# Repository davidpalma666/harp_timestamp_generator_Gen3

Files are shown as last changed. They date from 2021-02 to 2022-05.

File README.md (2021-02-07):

# Harp Timestamp Generator Gen3

This device generates programable timestamps to up to 6 harp devices.

Includes an internal battery to increase reliability for long term experiments.

# Licensing

The code, designs, documentation, and photos available in this repository is free: you can redistribute it and/or modify it under the terms of the used license.
Each subdirectory will contain a license or, possibly, a set of licenses if it involves both hardware and software. Check files named LICENSE.

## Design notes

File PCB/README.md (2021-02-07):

# Harp Timestamp Generator Gen1

## Licensing

The designs, documentation, and photos available in this repository are free: you can redistribute it and/or modify it under the terms of the used license.
Check file named LICENSE.

Copyright OEPS 2021

<br />This work is licensed under a <a rel="license" href="http://creativecommons.org/licenses/by-nc-sa/3.0/igo/">Creative Commons Attribution-NonCommercial-ShareAlike 3.0 IGO License</a>.

If your are interested in obtaining a license to sell this device, please contact info@oeps.tech

[1]: https://docs.google.com/spreadsheets/d/1aobmmEzBDethzIlrm1eg0eYkBqlyX3s9WbA9KgRwVQI/edit?usp=sharing

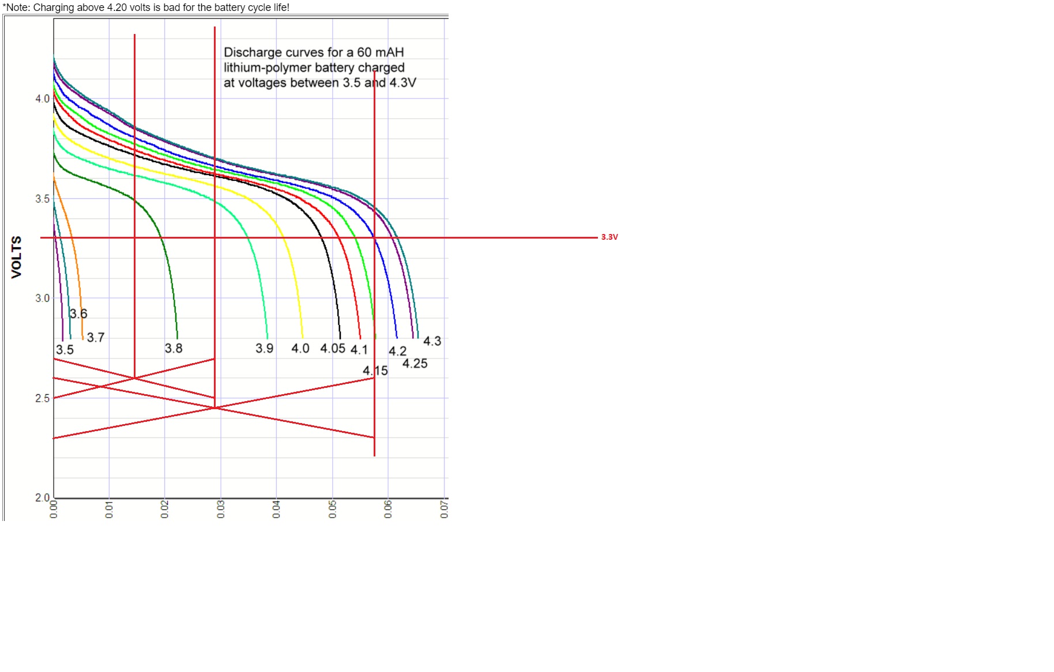
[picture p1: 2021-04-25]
Firmware/battery discharge curve.jpg

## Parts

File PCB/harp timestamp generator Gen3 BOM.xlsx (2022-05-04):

Qty | Value | Package | Parts | MPN | Type | Distributor | Distributor PN
ASSEMBLY HOUSE
1 | CFPA | CFPA | BUTTON | CFPA-1FB4-A2T | SMD | Digikey | 563-1246-1-ND
28 | 100nF | C0402 | C1, C3, C5, C7, C9, C12, C13, C14, C15, C16, C17, C18, C19, C20, C21, C22, C25, C26, C27, C28, C30, C31, C32, C35, C36, C37, C38, C62 | CGA2B3X7R1H104K050BB | SMD | Digikey | 445-6899-1-ND
5 | 4.7uF | C0603 | C8, C10, C11, C23, C24 | CRCW040210R0FKEDHP | SMD | Digikey | 541-10.0YCT-ND
1 | 4.7nF | C0402 | C2 | UMK105B7472KV-F | SMD | Digikey | 587-2237-1-ND
1 | 330nF | C0402 | C29 | GRM155R61A334KE15D | SMD | Digikey | 490-3263-1-ND
2 | 10n | C0402 | C33, C34 | CL05B103KB5NNNC | SMD | Digikey | 1276-1028-1-ND
2 | 47pF | C0402 | C4, C6 | 06035A470JAT2A | SMD | Digikey | 478-1171-1-ND
1 | 100u 25V | TT2D6 | C39 | EEUFM1E101B | TH | Digikey | P19702CT-ND
1 | 330pF | C0402 | C40 | C0402C331J5GACTU | SMD | Digikey | 399-7787-1-ND
7 | CLCK_JACK | 35RASMT2BHNTRX | CLKIN, CLKOUT0, CLKOUT1, CLKOUT2, CLKOUT3, CLKOUT4, CLKOUT5 | 35RASMT2BHNTRX | SMD | Digikey | SC1489-1-ND
1 | 330 Ohms @ 100MHz | R0603 | F1 | BLM18SG331TN1D | SMD | Digikey | 490-3997-1-ND
1 | MCP73831T-2ATI/OT | TSOT23-5 | IC1 | MCP73831T-2ATI/OT | SMD | Digikey | MCP73831T-2ATI/OTCT-ND
3 | SN74LVC1G125DBVT | SOT23-5 | IC10, IC18, IC19 | SN74LVC1G125DBVT | SMD | Digikey | 296-26595-1-ND
6 | SI8621BC-B-IS | SOIC8 | IC12, IC13, IC14, IC15, IC16, IC17 | Si8621BC-B-IS | SMD | Digikey | 336-2064-5-ND | Replacements: SI8621BB-B-IS
1 | USBLC6-2SC6 | SOT23-6L | IC2 | USBLC6-2SC6 | SMD | Digikey | 497-5235-1-ND
1 | FT232RL | SSOP28 | IC3 | FT232RL-REEL | SMD | Digikey | 768-1007-1-ND
1 | ICL7673CBAZA-T | SOIC8 | IC4 | ICL7673CBAZA-T | SMD | Digikey | ICL7673CBAZA-TCT-ND
2 | TLV70033DDCR | TSOT23-5 | IC5, IC11 | TLV70033DDCR | SMD | Digikey | 296-27937-6-ND
1 | ATXMEGA16A4U-AU | QFP80P1200X1200X120-44N | IC6 | ATXMEGA16A4U-AU | SMD | Digikey | ATXMEGA16A4U-AU-ND
3 | M74VHC1GT126DF1G | SC70-5 | IC7, IC8, IC9 | M74VHC1GT126DF1G | SMD | Digikey | M74VHC1GT126DF1GOSCT-ND
1 | 40R@100MHz | R0805 | L1 | MI0805K400R-10 | SMD | Digikey | 240-2389-1-ND
5 | 569-0112-100 | 569-011X-X00_LED_ARRAY | LED1, LED2, LED3, LED4, LED5 | 5690-111-100F | SMD | Digikey | 350-1782-ND
1 | OSCILLATOR | OSCILLATOR_3.2X2.5 | OSC1 | O 32,0-JT32C-A-K-3,3-LF | SMD | Digikey | 1908-1044-1-ND
1 | 2x3_header | MA03-2 | PDI | 67996-206HLF | TH | Digikey | 609-3210-ND
1 | RTU002P02T106 | SOT323 | Q1 | RTU002P02T106 | SMD | Digikey | RTU002P02T106CT-ND
1 | BC817-40W | SOT323-BEC | Q2 | BC817-40W,135 | SMD | Digikey | 1727-6185-1-ND
1 | BC817-40LT1SMD | SOT23-BEC | Q3 | SBC817-40LT1G | SMD | Digikey | SBC817-40LT1GOSCT-ND
1 | DMG1012UW | SOT323 | Q4 | DMG1012UW-7 | SMD | Digikey | DMG1012UW-7DICT-ND
1 | DMP2035U-7 | SOT323 | Q5 | DMP2035U-7 | SMD | Digikey | DMP2035U-7DICT-ND
1 | 1M | R0402 | R1 | CRCW04021M00FKEDC | SMD | Digikey | DMP2035U-7
3 | 100R | R0603 | R10, R11, R12 | RT0603DRD07100RL | SMD | Digikey | 311-100DCT-ND
3 | 4k5 | R0402 | R13, R17, R19 | RT0402BRD074K53L | SMD | Digikey | YAG1444CT-ND
1 | 20R | R2512 | R15 | CRM2512-FX-20R0ELF | SMD | Digikey | 118-CRM2512-FX-20R0ELFCT-ND
1 | 10R | R0402 | R2 | CRCW040210R0FKEDHP | SMD | Digikey | 541-10.0YCT-ND
13 | 1k | R0402 | R14, R21, R22, R23, R24, R25, R27, R28, R29, R30, R31, R54, R55 | CRCW04021K00FKED | SMD | Digikey | 541-1.00KYCT-ND
6 | 10k | R0402 | R3, R7, R9, R16, R18, R50 | CRCW040210K0FKEDC | SMD | Digikey | 541-3959-1-ND
10 | 330R | R0402 | R33, R34, R35, R36, R37, R40, R41, R42, R44, R45 | RC0402FR-07330RL | SMD | Digikey | 311-330LRCT-ND
1 | 51k 0.1% | R0402 | R4 | ERA-2AEB513X | SMD | Digikey | P51KDCCT-ND
1 | 15K 0.1% => 14k7 | R0402 | R5 | RT0402BRD0714K7L | SMD | Digikey | YAG4174CT-ND
2 | 100k | R0402 | R6, R48 | RC0603FR-07100KL | SMD | Digikey | 311-100KHRCT-ND
1 | I/O Header | ML10L | SV1 | SBH11-PBPC-D05-RA-BK | TH | Digikey | S9177-ND
10 | BC850 | SOT23 | T1, T2, T3, T4, T5, T6, T7, T8, T9, T10 | BC850C,215 | SMD | Digikey | 1727-4862-1-ND
1 | mini USB | 240-0002-1 | USB | UX60-MB-5S8 | SMD | Digikey | H2960TR-ND
1 | Switch SPDT | 7101MD9ABE | BATEN | 7101MD9ABE | TH | Digikey | CKN1045-ND
1 | B2B-PH-K-S(LF)(SN) | JST-XH-02-PACKAGE-ROUND-PAD | X1 | B2B-XH-A(LF)(SN) | SMD | Digikey | 455-2247-ND
POST-PRODUCTION
1 |  |  | Front Panel PCB | PCBWAY
1 |  |  | Rear Panel PCB | PCBWAY
1 |  |  | Enclosure | B5-080BK
1 |  |  | Battery lithium Polymer 2 Ah | MIKROE-1120 | - | Farnell | 2786900
4 |  |  | Bumper Cylindrical Dome 9.53mm | SJ-5306-CLEAR-3000/CASE
ACCESSORIES
3 |  |  | 3.5mm stereo jack cable 0.3 m, Black | P312-001 | - | Digikey | TL1621-ND
4 |  |  | 3.5mm stereo jack cable 1.2 m, Black | AV13646 |  | Farnell | 3712278
1 |  |  | 0.9 left angle USB cable | USB2HABM3RA |  | Farnell | 3402895
NOTES
 |  |  |  | Number of unique parts | 46
 |  |  |  | Number of SMD parts | 42
 |  |  |  | Number of TH parts | 4

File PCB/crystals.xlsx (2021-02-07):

Digikey PN | MNF PN | @25C [ppm] | Range of temperatures [ppm] | Supply Change [ppm] | Load Change [ppm] | Aging/year [ppm] |  | Dimensions [mm] | Pinout | Current [mA] | Type
XC2259CT-ND | ECS-TXO-2520-33-320-AN-TR | 2 | 2.5 | 0.2 | 0.2 | 1 | 5.9 | 2.5 x 2.0 | En/Dis, GND, OUT, VDD | 6 | HCMOS TXCO
1908-1044-1-ND | O 32,0-JT32C-A-K-3,3-LF | 0.5 | 2.5 | 0.2 | 0.2 | 1 | 4.4 | 3.2 x 2.5 | En/Dis, GND, OUT, VDD | 4.8 | HCMOS TXCO
50-ECS-TXO-2520MV-320-AN-CT-ND | ECS-TXO-2520MV-320-AN-TR | 1.5 | 2.5 | 0.3 | 0.3 | 1 | 5.6 | 2.5 x 2.0 | En/Dis, GND, OUT, VDD | 6 | CMOS TXCO
50-ECS-TXO-2520MV-320-AY-CT-ND | ECS-TXO-2520MV-320-AY-TR | 1.5 | 2.5 | 0.3 | 0.3 | 1 | 5.6 | 2.5 x 2.0 | En/Dis, GND, OUT, VDD | 6 | CMOS TXCO
50-ECS-TXO-25CSMV-320-BM-CT-ND | ECS-TXO-25CSMV-320-BM-TR | 2 | 1 | 0.2 | 0.2 | 1 | 4.4 | 2.5 x 2.0 | GND, GND, OUT, VDD | 2.5 | Clipped Sinewave TSCO

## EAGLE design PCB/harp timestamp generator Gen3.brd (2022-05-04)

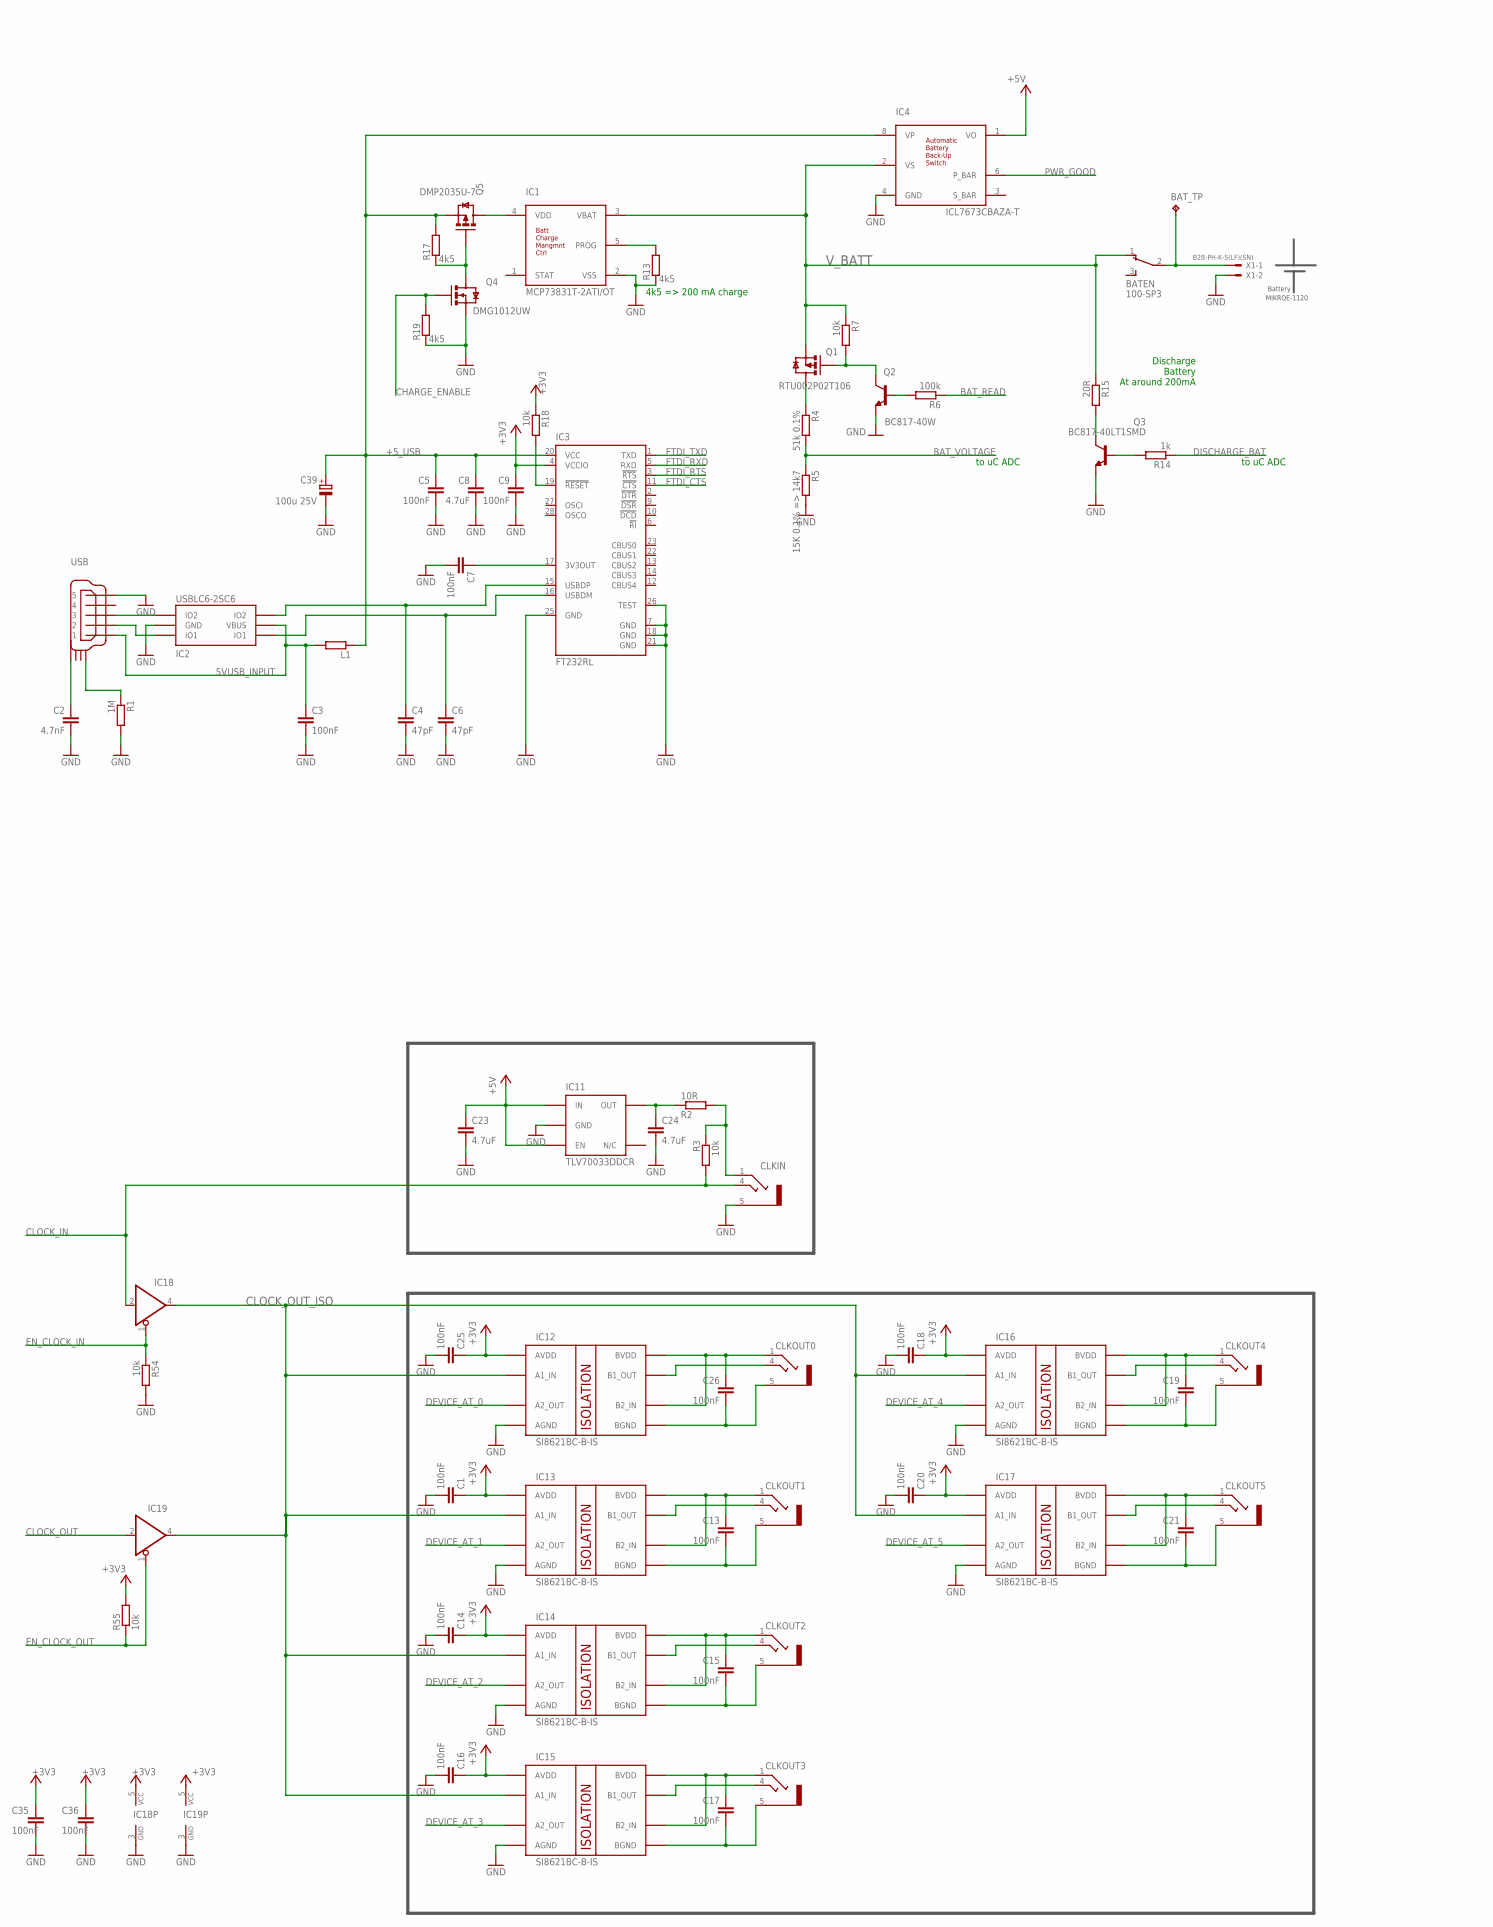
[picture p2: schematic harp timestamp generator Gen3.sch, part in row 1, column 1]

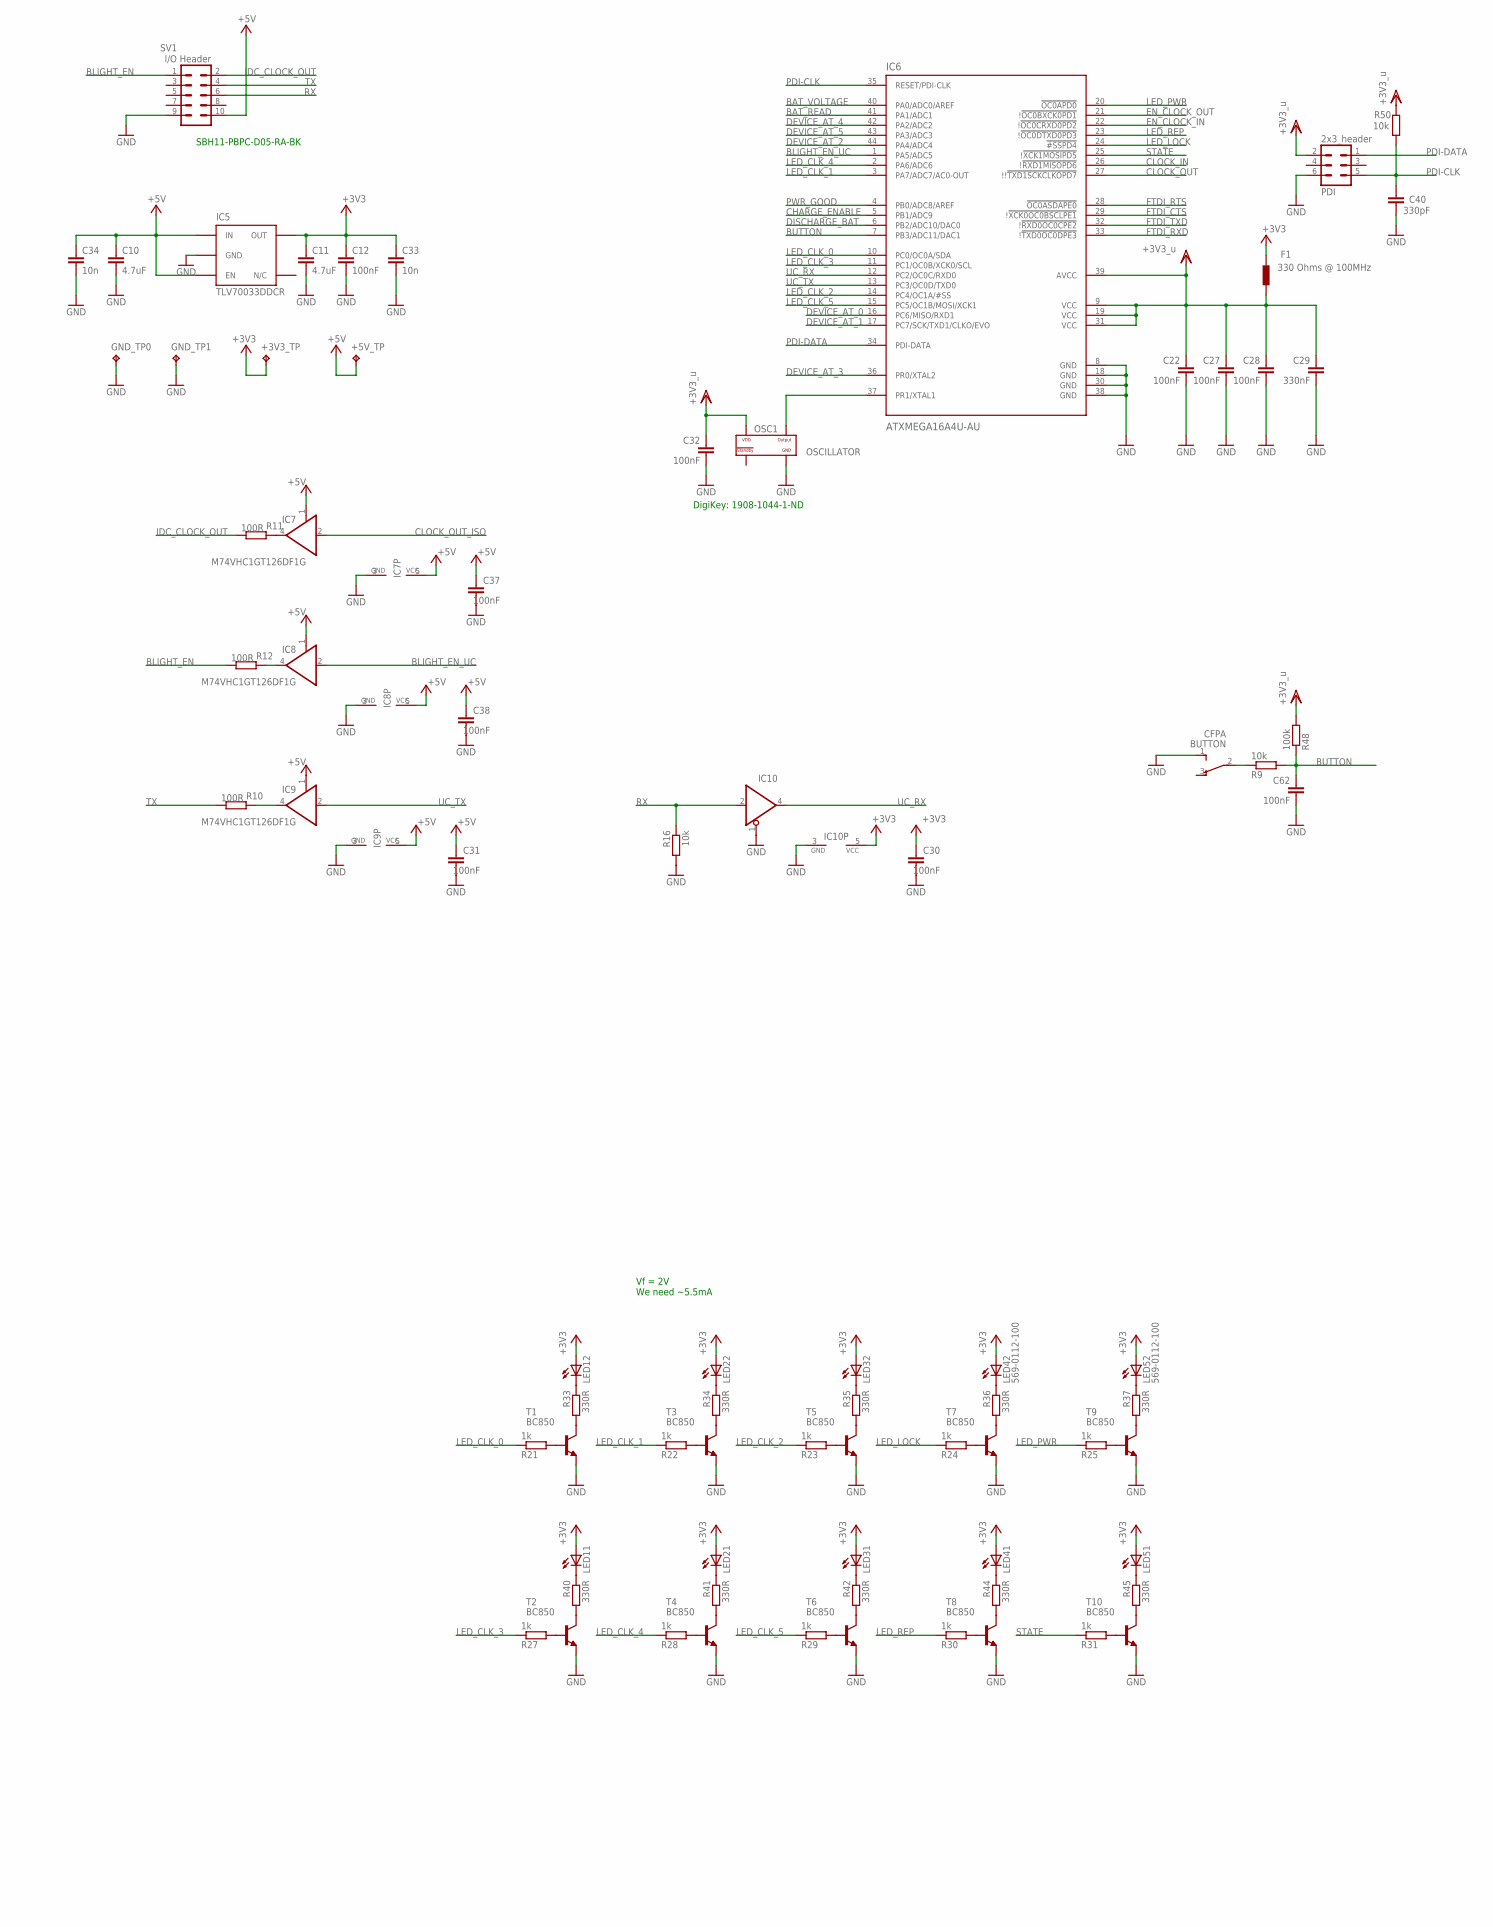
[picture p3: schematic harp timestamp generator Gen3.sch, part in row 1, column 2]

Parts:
+3V3_TP, +5V_TP: TPPAD1-13; P1-13; MPN n.a.
BATEN: 100-SP3; 2M1-SP1-T2-B4-M6RE
BAT_TP: TPPAD1-13; P1-13; MPN n.a.
BUTTON: CFPA; MPN CFPA-1FB4-A2T
C1, C3, C5, C7, C9, C12, C13, C14, C15, C16, C17, C18, C19, C20, C21, C22, C25, C26, C27, C28, C30, C31, C32, C35, C36, C37, C38, C62: 100nF; C0402; MPN CGA2B3X7R1H104K050BB
C2: 4.7nF; C0402; MPN UMK105B7472KV-F
C4, C6: 47pF; C0402; MPN 04025A470JAT2A
C8, C10, C11, C23, C24: 4.7uF; C0603; MPN EMK107ABJ475KA-T
C29: 330nF; C0402; MPN GRM155R61A334KE15D
C33, C34: 10n; C0402; MPN CL05B103KB5NNNC
C39: 100u 25V; TT2D6; MPN EEUFM1E101B
C40: 330pF; C0402; MPN C0402C331J5GACTU
CLKIN: CLCK_JACK; 35RASMT2BHNTRX; MPN 35RASMT2BHNTRX
CLKOUT0, CLKOUT1, CLKOUT2, CLKOUT3, CLKOUT4, CLKOUT5: CLCK_JACK; 35RASMT2BHNTRX; MPN 35RASMT2BHNTRX
F1: 330 Ohms @ 100MHz; R0603; MPN BLM18SG331TN1D
GND_TP0, GND_TP1: TPPAD1-13; P1-13; MPN n.a.
IC1: MCP73831T-2ATI/OT; TSOT23-5
IC2: USBLC6-2SC6; SOT23-6L; MPN USBLC6-2SC6
IC3: FT232RL; SSOP28; MPN FT232RL-REEL
IC4: ICL7673CBAZA-T; SOIC8; MPN ICL7673CBAZA-T
IC5, IC11: TLV70033DDCR; TSOT23-5; MPN TLV70033DDCR
IC6: ATXMEGA16A4U-AU; QFP80P1200X1200X120-44N; MPN ATXMEGA16A4U-AU
IC7, IC8, IC9: M74VHC1GT126DF1G; SC70-5; MPN M74VHC1GT126DF1G
IC10, IC18, IC19: SN74LVC1G125DBVT; SOT23-5; MPN SN74LVC1G125DBVT
IC12, IC13, IC14, IC15, IC16, IC17: SI8621BC-B-IS; SOIC8; MPN Si8621BC-B-IS
L1: 40R@100MHz; R0805; MPN MI0805K400R-10
LED1, LED2, LED3, LED4, LED5: 569-0112-100; 569-011X-X00_LED_ARRAY; MPN 5690-111-100F
OSC1: OSCILLATOR; OSCILLATOR_3.2X2.5; MPN O 32,0-JT32C-A-K-3,3-LF
PDI: 2x3_header; MA03-2; MPN 67996-206HLF
Q1: RTU002P02T106; SOT323; MPN RTU002P02T106
Q2: BC817-40W; SOT323-BEC; MPN BC817-40W,135
Q3: BC817-40LT1SMD; SOT23-BEC; MPN SBC817-40LT1G
Q4: DMG1012UW; SOT323; MPN DMG1012UW-7
Q5: DMP2035U-7; SOT323
R1: 1M; R0402; MPN CRCW04021M00FKEDC
R2: 10R; R0402; MPN CRCW040210R0FKEDHP
R3, R7, R9, R16, R18: 10k; R0402; MPN CRCW040210K0FKEDC
R4: 51k 0.1%; R0402; MPN ERA-2AEB513X
R5: 15K 0.1% => 14k7; R0402; MPN RT0402BRD0714K7L
R6, R48: 100k; R0402; MPN ERJ-2RHD1002X
R10, R11, R12: 100R; R0603; MPN RT0603DRD07100RL
R13, R17, R19: 4k5; R0402; MPN RT0402BRD074K53L
R14: 1k; R0402; MPN CRCW040210K0FKEDC
R15: 20R; R2512; MPN RCP2512W25R0GEB
R21, R22, R23, R24, R25, R27, R28, R29, R30, R31: 1k; R0402; MPN CRCW04021K00FKEDHP
R33, R34, R35, R36, R37, R40, R41, R42, R44, R45: 330R; R0402; MPN RC0402FR-07330RL
R50: 10k; R0402; MPN CRCW040210K0FKED
R54, R55: 10k; R0402; MPN CRCW04021K00FKEDHP
SV1: I/O Header; ML10L; MPN SBH11-PBPC-D05-RA-BK
T1, T2, T3, T4, T5, T6, T7, T8, T9, T10: BC850; SOT23; MPN BC850C,215
USB: mini USB; 240-0002-1; MPN UX60-MB-5S8
X1: B2B-PH-K-S(LF)(SN); JST-XH-02-PACKAGE-ROUND-PAD; MPN B2B-PH-K-S(LF)(SN)

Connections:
5VUSB_INPUT: C3.1, IC2.P$5 (VBUS), L1.2, USB.P$1 (1)
+3V3: +3V3_TP.TP, C1.1, C9.1, C11.1, C12.1, C14.1, C16.1, C18.1, C20.1, C25.1, C30.1, C33.1, C35.1, C36.1, F1.2, IC3.4 (VCCIO), IC5.5 (OUT), IC10.5 (VCC), IC12.1 (AVDD), IC13.1 (AVDD), IC14.1 (AVDD), IC15.1 (AVDD), IC16.1 (AVDD), IC17.1 (AVDD), IC18.5 (VCC), IC19.5 (VCC), LED1.A1 (A), LED1.A2 (A), LED2.A1 (A), LED2.A2 (A), LED3.A1 (A), LED3.A2 (A), LED4.A1 (A), LED4.A2 (A), LED5.A1 (A), LED5.A2 (A), R18.1, R55.2
+5V: +5V_TP.TP, C10.1, C23.1, C31.1, C34.1, C37.1, C38.1, IC4.1 (VO), IC5.1 (IN), IC5.3 (EN), IC7.1 (OE), IC7.5 (VCC), IC8.1 (OE), IC8.5 (VCC), IC9.1 (OE), IC9.5 (VCC), IC11.1 (IN), IC11.3 (EN), SV1.10
+5_USB: C5.1, C8.1, C39.+, IC3.20 (VCC), IC4.8 (VP), L1.1, Q5.1 (S), R17.2
BAT_READ: IC6.41 (PA1/ADC1), R6.1
BAT_VOLTAGE: IC6.40 (PA0/ADC0/AREF), R4.2, R5.1
BLIGHT_EN: R12.1, SV1.1
BLIGHT_EN_UC: IC6.1 (PA5/ADC5), IC8.2 (I)
BUTTON: C62.1, IC6.7 (PB3/ADC11/DAC1), R9.2, R48.1
CHARGE_ENABLE: IC6.5 (PB1/ADC9), Q4.2 (G), R19.2
CLKOUT0: CLKOUT0.4, IC12.7 (B1_OUT)
CLKOUT1: CLKOUT1.4, IC13.7 (B1_OUT)
CLKOUT2: CLKOUT2.4, IC14.7 (B1_OUT)
CLKOUT3: CLKOUT3.4, IC15.7 (B1_OUT)
CLKOUT4: CLKOUT4.4, IC16.7 (B1_OUT)
CLKOUT5: CLKOUT5.4, IC17.7 (B1_OUT)
CLOCK_IN: CLKIN.4, IC6.26 (!!RXD1MISOPD6), IC18.2 (I), R3.2
CLOCK_OUT: IC6.27 (!!!TXD1SCKCLKOPD7), IC19.2 (I)
CLOCK_OUT_ISO: IC7.2 (I), IC12.2 (A1_IN), IC13.2 (A1_IN), IC14.2 (A1_IN), IC15.2 (A1_IN), IC16.2 (A1_IN), IC17.2 (A1_IN), IC18.4 (O), IC19.4 (O)
DEVICE_AT_0: IC6.16 (PC6/MISO/RXD1), IC12.3 (A2_OUT)
DEVICE_AT_1: IC6.17 (PC7/SCK/TXD1/CLKO/EVO), IC13.3 (A2_OUT)
DEVICE_AT_2: IC6.44 (PA4/ADC4), IC14.3 (A2_OUT)
DEVICE_AT_3: IC6.36 (PR0/XTAL2), IC15.3 (A2_OUT)
DEVICE_AT_4: IC6.42 (PA2/ADC2), IC16.3 (A2_OUT)
DEVICE_AT_5: IC6.43 (PA3/ADC3), IC17.3 (A2_OUT)
DISCHARGE_BAT: IC6.6 (PB2/ADC10/DAC0), R14.1
EN_CLOCK_IN: IC6.22 (!!OC0CRXD0PD2), IC18.1 (OE), R54.1
EN_CLOCK_OUT: IC6.21 (!!OC0BXCK0PD1), IC19.1 (OE), R55.1
FTDI_CTS: IC3.11 (!CTS), IC6.29 (!!XCK0OC0BSCLPE1)
FTDI_RTS: IC3.3 (!RTS), IC6.28 (!OC0ASDAPE0)
FTDI_RXD: IC3.5 (RXD), IC6.33 (!!TXD0OC0DPE3)
FTDI_TXD: IC3.1 (TXD), IC6.32 (!!RXD0OC0CPE2)
GND: BUTTON.1 (3), C1.2, C2.2, C3.2, C4.2, C5.2, C6.2, C7.2, C8.2, C9.2, C10.2, C11.2, C12.2, C14.2, C16.2, C18.2, C20.2, C22.2, C23.2, C24.2, C25.2, C27.2, C28.2, C29.2, C30.2, C31.2, C32.2, C33.2, C34.2, C35.2, C36.2, C37.2, C38.2, C39.-, C40.2, C62.2, CLKIN.5, GND_TP0.TP, GND_TP1.TP, IC1.2 (VSS), IC2.P$2 (GND), IC3.7 (GND), IC3.18 (GND), IC3.21 (GND), IC3.25 (GND), IC3.26 (TEST), IC4.4 (GND), IC5.2 (GND), IC6.8 (GND), IC6.18 (GND), IC6.30 (GND), IC6.38 (GND), IC7.3 (GND), IC8.3 (GND), IC9.3 (GND), IC10.1 (OE), IC10.3 (GND), IC11.2 (GND), IC12.4 (AGND), IC13.4 (AGND), IC14.4 (AGND), IC15.4 (AGND), IC16.4 (AGND), IC17.4 (AGND), IC18.3 (GND), IC19.3 (GND), OSC1.P$2 (GND), PDI.6, Q2.E, Q3.E, Q4.1 (S), R1.2, R5.2, R13.1, R16.2, R19.1, R54.2, SV1.9, T1.2 (E), T2.2 (E), T3.2 (E), T4.2 (E), T5.2 (E), T6.2 (E), T7.2 (E), T8.2 (E), T9.2 (E), T10.2 (E), USB.P$5 (5), X1.2
GND_ISO: C26.2, CLKOUT0.5, IC12.5 (BGND)
GND_ISO1: C13.2, CLKOUT1.5, IC13.5 (BGND)
GND_ISO2: C15.2, CLKOUT2.5, IC14.5 (BGND)
GND_ISO3: C17.2, CLKOUT3.5, IC15.5 (BGND)
GND_ISO4: C19.2, CLKOUT4.5, IC16.5 (BGND)
GND_ISO5: C21.2, CLKOUT5.5, IC17.5 (BGND)
IDC_CLOCK_OUT: R11.1, SV1.2
LED_CLK_0: IC6.10 (PC0/OC0A/SDA), R21.1
LED_CLK_1: IC6.3 (PA7/ADC7/AC0-OUT), R22.1
LED_CLK_2: IC6.14 (PC4/OC1A/#SS), R23.1
LED_CLK_3: IC6.11 (PC1/OC0B/XCK0/SCL), R27.1
LED_CLK_4: IC6.2 (PA6/ADC6), R28.1
LED_CLK_5: IC6.15 (PC5/OC1B/MOSI/XCK1), R29.1
LED_LOCK: IC6.24 (!#SSPD4), R24.1
LED_PWR: IC6.20 (!OC0APD0), R25.1
LED_REP: IC6.23 (!!OC0DTXD0PD3), R30.1
unnamed: R24.2, T7.1 (B)
unnamed: Q4.3 (D), Q5.2 (G), R17.1
unnamed: IC8.4 (O), R12.2
unnamed: IC9.4 (O), R10.2
unnamed: C26.1, CLKOUT0.1, IC12.6 (B2_IN), IC12.8 (BVDD)
unnamed: C13.1, CLKOUT1.1, IC13.6 (B2_IN), IC13.8 (BVDD)
unnamed: R36.2, T7.3 (C)
unnamed: IC7.4 (O), R11.2
unnamed: IC1.4 (VDD), Q5.3 (D)
unnamed: C15.1, CLKOUT2.1, IC14.6 (B2_IN), IC14.8 (BVDD)
unnamed: R22.2, T3.1 (B)
unnamed: IC1.5 (PROG), R13.2
unnamed: R21.2, T1.1 (B)
unnamed: LED3.C1 (C), R42.1
unnamed: R33.2, T1.3 (C)
unnamed: R27.2, T2.1 (B)
unnamed: R34.2, T3.3 (C)
unnamed: R40.2, T2.3 (C)
unnamed: LED3.C2 (C), R35.1
unnamed: R28.2, T4.1 (B)
unnamed: R41.2, T4.3 (C)
unnamed: R23.2, T5.1 (B)
unnamed: R35.2, T5.3 (C)
unnamed: R29.2, T6.1 (B)
unnamed: R42.2, T6.3 (C)
unnamed: LED1.C2 (C), R33.1
unnamed: LED2.C2 (C), R34.1
unnamed: LED1.C1 (C), R40.1
unnamed: LED2.C1 (C), R41.1
unnamed: R30.2, T8.1 (B)
unnamed: Q3.B, R14.2
unnamed: Q3.C, R15.2
unnamed: C17.1, CLKOUT3.1, IC15.6 (B2_IN), IC15.8 (BVDD)
unnamed: C7.1, IC3.17 (3V3OUT)
unnamed: IC2.P$1 (IO1), USB.P$2 (2)
unnamed: CLKIN.1, R2.2, R3.1
unnamed: C24.1, IC11.5 (OUT), R2.1
unnamed: BUTTON.2, R9.1
unnamed: C19.1, CLKOUT4.1, IC16.6 (B2_IN), IC16.8 (BVDD)
unnamed: R44.2, T8.3 (C)
unnamed: C21.1, CLKOUT5.1, IC17.6 (B2_IN), IC17.8 (BVDD)
unnamed: IC2.P$3 (IO2), USB.P$3 (3)
unnamed: R25.2, T9.1 (B)
unnamed: R37.2, T9.3 (C)
unnamed: R31.2, T10.1 (B)
unnamed: C2.1, USB.SHIELD_4
unnamed: R45.2, T10.3 (C)
unnamed: R1.1, USB.SHIELD_1
unnamed: LED5.C1 (C), R45.1
unnamed: LED5.C2 (C), R37.1
unnamed: LED4.C2 (C), R36.1
unnamed: LED4.C1 (C), R44.1
unnamed: BATEN.2, BAT_TP.TP, X1.1
unnamed: Q1.3 (D), R4.1
unnamed: Q1.2 (G), Q2.C, R7.2
unnamed: Q2.B, R6.2
unnamed: IC3.19 (!RESET), R18.2
OSC1: IC6.37 (PR1/XTAL1), OSC1.P$3 (OUTPUT)
PDI-CLK: C40.1, IC6.35 (RESET/PDI-CLK), PDI.5, R50.1
PDI-DATA: IC6.34 (PDI-DATA), PDI.1
PWR_GOOD: IC4.6 (P_BAR), IC6.4 (PB0/ADC8/AREF)
RX: IC10.2 (I), R16.1, SV1.6
STATE: IC6.25 (!!XCK1MOSIPD5), R31.1
TX: R10.1, SV1.4
UC_RX: IC6.12 (PC2/OC0C/RXD0), IC10.4 (O)
UC_TX: IC6.13 (PC3/OC0D/TXD0), IC9.2 (I)
USBDM: C6.1, IC2.P$6 (IO1), IC3.16 (USBDM)
USBDP: C4.1, IC2.P$4 (IO2), IC3.15 (USBDP)
VDD: C22.1, C27.1, C28.1, C29.1, C32.1, F1.1, IC6.9 (VCC), IC6.19 (VCC), IC6.31 (VCC), IC6.39 (AVCC), OSC1.P$4 (VDD), PDI.2, R48.2, R50.2
V_BATT: BATEN.1, IC1.3 (VBAT), IC4.2 (VS), Q1.1 (S), R7.1, R15.1

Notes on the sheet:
Vf = 2V We need ~5.5mA
SBH11-PBPC-D05-RA-BK
4k5 => 200 mA charge
Battery
to uC ADC
MIKROE-1120
Discharge Battery At around 200mA
DigiKey: 1908-1044-1-ND

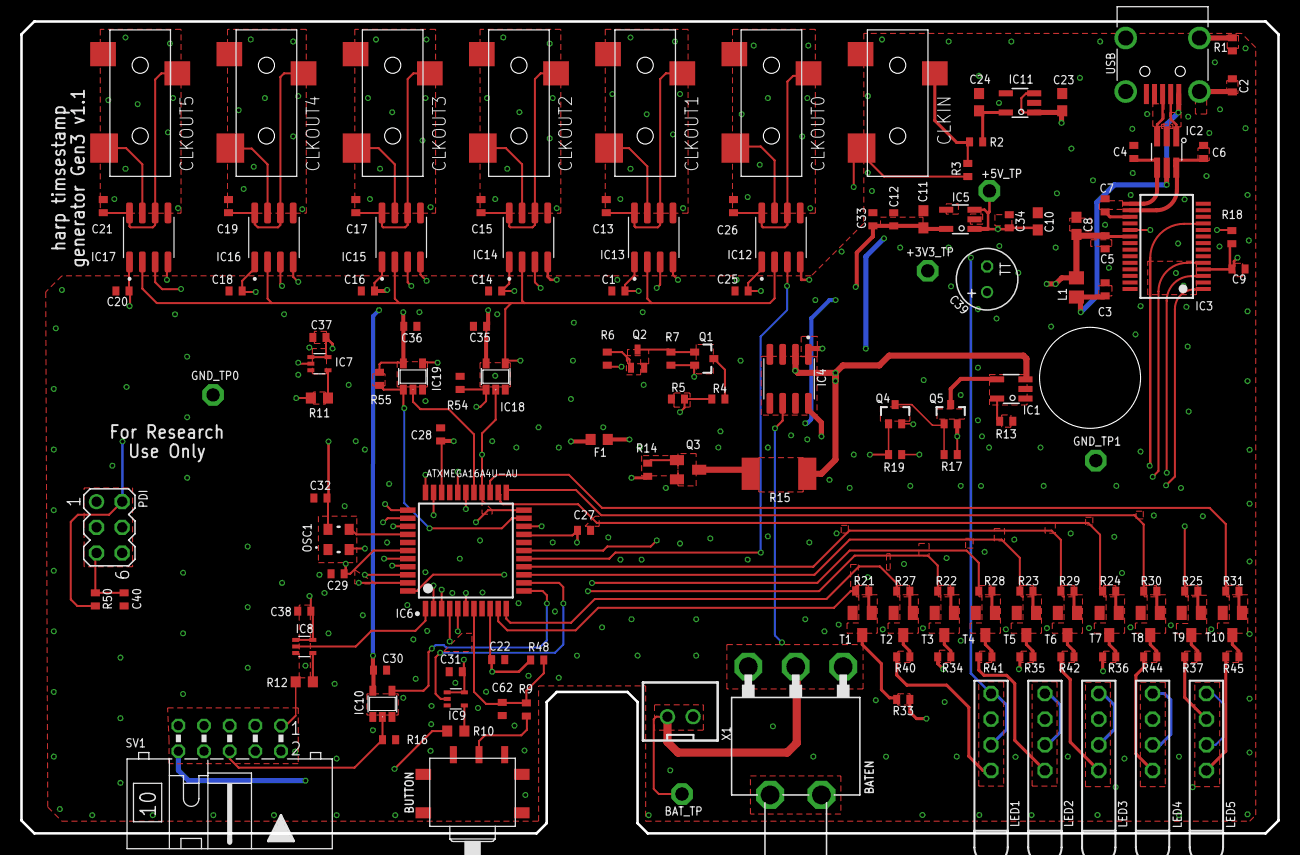
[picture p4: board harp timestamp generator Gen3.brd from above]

Board: 4 copper layers, 124.5 x 80.4 mm, 143 parts (0 on the bottom side), 119 nets.

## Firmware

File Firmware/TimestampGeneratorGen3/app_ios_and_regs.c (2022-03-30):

#include <avr/io.h>
#include "hwbp_core_types.h"
#include "app_ios_and_regs.h"

/************************************************************************/
/* Configure and initialize IOs                                         */
/************************************************************************/
void init_ios(void)
{	/* Configure input pins */
	io_pin2in(&PORTA, 2, PULL_IO_TRISTATE, SENSE_IO_NO_INT_USED);        // DEVICE_AT_4
	io_pin2in(&PORTA, 3, PULL_IO_TRISTATE, SENSE_IO_NO_INT_USED);        // DEVICE_AT_5
	io_pin2in(&PORTA, 4, PULL_IO_TRISTATE, SENSE_IO_NO_INT_USED);        // DEVICE_AT_2
	io_pin2in(&PORTB, 0, PULL_IO_UP, SENSE_IO_EDGES_BOTH);               // POWER_GOOD
	io_pin2in(&PORTB, 3, PULL_IO_TRISTATE, SENSE_IO_EDGES_BOTH);         // BUTTON
	io_pin2in(&PORTC, 6, PULL_IO_TRISTATE, SENSE_IO_NO_INT_USED);        // DEVICE_AT_0
	io_pin2in(&PORTC, 7, PULL_IO_TRISTATE, SENSE_IO_NO_INT_USED);        // DEVICE_AT_1
	io_pin2in(&PORTR, 0, PULL_IO_TRISTATE, SENSE_IO_NO_INT_USED);        // DEVICE_AT_3

	/* Configure input interrupts */
	io_set_int(&PORTB, INT_LEVEL_LOW, 0, (1<<0), false);                 // POWER_GOOD

	/* Configure output pins */
	io_pin2out(&PORTA, 1, OUT_IO_DIGITAL, IN_EN_IO_EN);                  // BAT_READ
	io_pin2out(&PORTA, 5, OUT_IO_DIGITAL, IN_EN_IO_EN);                  // EN_SCREEN_BACKLIGHT
	io_pin2out(&PORTA, 6, OUT_IO_DIGITAL, IN_EN_IO_EN);                  // LED_CLK_4
	io_pin2out(&PORTA, 7, OUT_IO_DIGITAL, IN_EN_IO_EN);                  // LED_CLK_1
	io_pin2out(&PORTB, 1, OUT_IO_DIGITAL, IN_EN_IO_EN);                  // EN_CHARGE
	io_pin2out(&PORTB, 2, OUT_IO_DIGITAL, IN_EN_IO_EN);                  // EN_DISCHARGE
	io_pin2out(&PORTC, 0, OUT_IO_DIGITAL, IN_EN_IO_EN);                  // LED_CLK_0
	io_pin2out(&PORTC, 1, OUT_IO_DIGITAL, IN_EN_IO_EN);                  // LED_CLK_3
	io_pin2out(&PORTC, 4, OUT_IO_DIGITAL, IN_EN_IO_EN);                  // LED_CLK_2
	io_pin2out(&PORTC, 5, OUT_IO_DIGITAL, IN_EN_IO_EN);                  // LED_CLK_5
	io_pin2out(&PORTD, 0, OUT_IO_DIGITAL, IN_EN_IO_EN);                  // LED_POWER
	io_pin2out(&PORTD, 1, OUT_IO_DIGITAL, IN_EN_IO_EN);                  // EN_CLOCK_OUT
	io_pin2out(&PORTD, 2, OUT_IO_DIGITAL, IN_EN_IO_EN);                  // EN_CLOCK_IN
	io_pin2out(&PORTD, 3, OUT_IO_DIGITAL, IN_EN_IO_EN);                  // LED_REPEATER
	io_pin2out(&PORTD, 4, OUT_IO_DIGITAL, IN_EN_IO_EN);                  // LED_LOCK
	io_pin2out(&PORTD, 5, OUT_IO_DIGITAL, IN_EN_IO_EN);                  // LED_STATE

	/* Initialize output pins */
	clr_BAT_READ;
	clr_EN_SCREEN_BACKLIGHT;
	clr_LED_CLK_4;
	clr_LED_CLK_1;
	clr_EN_CHARGE;
	clr_EN_DISCHARGE;
	clr_LED_CLK_0;
	clr_LED_CLK_3;
	clr_LED_CLK_2;
	clr_LED_CLK_5;
	clr_LED_POWER;
	clr_EN_CLOCK_OUT;
	set_EN_CLOCK_IN;
	clr_LED_REPEATER;
	clr_LED_LOCK;
	clr_LED_STATE;
}

/************************************************************************/
/* Registers' stuff                                                     */
/************************************************************************/
AppRegs app_regs;

uint8_t app_regs_type[] = {
	TYPE_U8,
	TYPE_U8,
	TYPE_U8,
	TYPE_U8,
	TYPE_FLOAT,
	TYPE_FLOAT,
	TYPE_FLOAT,
	TYPE_U16,
	TYPE_U16
};

uint16_t app_regs_n_elements[] = {
	1,
	1,
	1,
	1,
	1,
	1,
	1,
	1,
	1
};

uint8_t *app_regs_pointer[] = {
	(uint8_t*)(&app_regs.REG_CONFIG),
	(uint8_t*)(&app_regs.REG_DEVICES_CONNECTED),
	(uint8_t*)(&app_regs.REG_REPEATER_STATUS),
	(uint8_t*)(&app_regs.REG_BATTERY_RATE),
	(uint8_t*)(&app_regs.REG_BATTERY),
	(uint8_t*)(&app_regs.REG_BATTERY_TH_LOW),
	(uint8_t*)(&app_regs.REG_BATTERY_TH_HIGH),
	(uint8_t*)(&app_regs.REG_BATTERY_CALIBRATION0),
	(uint8_t*)(&app_regs.REG_BATTERY_CALIBRATION1)
};

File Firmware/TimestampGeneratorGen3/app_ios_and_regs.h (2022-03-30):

#ifndef _APP_IOS_AND_REGS_H_
#define _APP_IOS_AND_REGS_H_
#include "cpu.h"

void init_ios(void);
/************************************************************************/
/* Definition of input pins                                             */
/************************************************************************/
// DEVICE_AT_4            Description: Device is connected to CLKOUT4
// DEVICE_AT_5            Description: Device is connected to CLKOUT5
// DEVICE_AT_2            Description: Device is connected to CLKOUT2
// POWER_GOOD             Description: Detects the presence of the USB power
// BUTTON                 Description: User's input button
// DEVICE_AT_0            Description: Device is connected to CLKOUT0
// DEVICE_AT_1            Description: Device is connected to CLKOUT1
// DEVICE_AT_3            Description: Device is connected to CLKOUT3

#define read_DEVICE_AT_4 read_io(PORTA, 2)      // DEVICE_AT_4
#define read_DEVICE_AT_5 read_io(PORTA, 3)      // DEVICE_AT_5
#define read_DEVICE_AT_2 read_io(PORTA, 4)      // DEVICE_AT_2
#define read_POWER_GOOD read_io(PORTB, 0)       // POWER_GOOD
#define read_BUTTON read_io(PORTB, 3)           // BUTTON
#define read_DEVICE_AT_0 read_io(PORTC, 6)      // DEVICE_AT_0
#define read_DEVICE_AT_1 read_io(PORTC, 7)      // DEVICE_AT_1
#define read_DEVICE_AT_3 read_io(PORTR, 0)      // DEVICE_AT_3

/************************************************************************/
/* Definition of output pins                                            */
/************************************************************************/
// BAT_READ               Description: 
// EN_SCREEN_BACKLIGHT    Description: 
// LED_CLK_4              Description: 
// LED_CLK_1              Description: 
// EN_CHARGE              Description: 
// EN_DISCHARGE           Description: 
// LED_CLK_0              Description: 
// LED_CLK_3              Description: 
// LED_CLK_2              Description: 
// LED_CLK_5              Description: 
// LED_POWER              Description: 
// EN_CLOCK_OUT           Description: 
// EN_CLOCK_IN            Description: 
// LED_REPEATER           Description: 
// LED_LOCK               Description: 
// LED_STATE              Description: 

/* BAT_READ */
#define set_BAT_READ set_io(PORTA, 1)
#define clr_BAT_READ clear_io(PORTA, 1)
#define tgl_BAT_READ toggle_io(PORTA, 1)
#define read_BAT_READ read_io(PORTA, 1)

/* EN_SCREEN_BACKLIGHT */
#define set_EN_SCREEN_BACKLIGHT set_io(PORTA, 5)
#define clr_EN_SCREEN_BACKLIGHT clear_io(PORTA, 5)
#define tgl_EN_SCREEN_BACKLIGHT toggle_io(PORTA, 5)
#define read_EN_SCREEN_BACKLIGHT read_io(PORTA, 5)

/* LED_CLK_4 */
#define set_LED_CLK_4 set_io(PORTA, 6)
#define clr_LED_CLK_4 clear_io(PORTA, 6)
#define tgl_LED_CLK_4 toggle_io(PORTA, 6)
#define read_LED_CLK_4 read_io(PORTA, 6)

/* LED_CLK_1 */
#define set_LED_CLK_1 set_io(PORTA, 7)
#define clr_LED_CLK_1 clear_io(PORTA, 7)
#define tgl_LED_CLK_1 toggle_io(PORTA, 7)
#define read_LED_CLK_1 read_io(PORTA, 7)

/* EN_CHARGE */
#define set_EN_CHARGE set_io(PORTB, 1)
#define clr_EN_CHARGE clear_io(PORTB, 1)
#define tgl_EN_CHARGE toggle_io(PORTB, 1)
#define read_EN_CHARGE read_io(PORTB, 1)

/* EN_DISCHARGE */
#define set_EN_DISCHARGE set_io(PORTB, 2)
#define clr_EN_DISCHARGE clear_io(PORTB, 2)
#define tgl_EN_DISCHARGE toggle_io(PORTB, 2)
#define read_EN_DISCHARGE read_io(PORTB, 2)

/* LED_CLK_0 */
#define set_LED_CLK_0 set_io(PORTC, 0)
#define clr_LED_CLK_0 clear_io(PORTC, 0)
#define tgl_LED_CLK_0 toggle_io(PORTC, 0)
#define read_LED_CLK_0 read_io(PORTC, 0)

/* LED_CLK_3 */
#define set_LED_CLK_3 set_io(PORTC, 1)
#define clr_LED_CLK_3 clear_io(PORTC, 1)
#define tgl_LED_CLK_3 toggle_io(PORTC, 1)
#define read_LED_CLK_3 read_io(PORTC, 1)

/* LED_CLK_2 */
#define set_LED_CLK_2 set_io(PORTC, 4)
#define clr_LED_CLK_2 clear_io(PORTC, 4)
#define tgl_LED_CLK_2 toggle_io(PORTC, 4)
#define read_LED_CLK_2 read_io(PORTC, 4)

/* LED_CLK_5 */
#define set_LED_CLK_5 set_io(PORTC, 5)
#define clr_LED_CLK_5 clear_io(PORTC, 5)
#define tgl_LED_CLK_5 toggle_io(PORTC, 5)
#define read_LED_CLK_5 read_io(PORTC, 5)

/* LED_POWER */
#define set_LED_POWER set_io(PORTD, 0)
#define clr_LED_POWER clear_io(PORTD, 0)
#define tgl_LED_POWER toggle_io(PORTD, 0)
#define read_LED_POWER read_io(PORTD, 0)

/* EN_CLOCK_OUT */
#define set_EN_CLOCK_OUT clear_io(PORTD, 1)
#define clr_EN_CLOCK_OUT set_io(PORTD, 1)
#define tgl_EN_CLOCK_OUT toggle_io(PORTD, 1)
#define read_EN_CLOCK_OUT read_io(PORTD, 1)

/* EN_CLOCK_IN */
#define set_EN_CLOCK_IN clear_io(PORTD, 2)
#define clr_EN_CLOCK_IN set_io(PORTD, 2)
#define tgl_EN_CLOCK_IN toggle_io(PORTD, 2)
#define read_EN_CLOCK_IN read_io(PORTD, 2)

/* LED_REPEATER */
#define set_LED_REPEATER set_io(PORTD, 3)
#define clr_LED_REPEATER clear_io(PORTD, 3)
#define tgl_LED_REPEATER toggle_io(PORTD, 3)
#define read_LED_REPEATER read_io(PORTD, 3)

/* LED_LOCK */
#define set_LED_LOCK set_io(PORTD, 4)
#define clr_LED_LOCK clear_io(PORTD, 4)
#define tgl_LED_LOCK toggle_io(PORTD, 4)
#define read_LED_LOCK read_io(PORTD, 4)

/* LED_STATE */
#define set_LED_STATE set_io(PORTD, 5)
#define clr_LED_STATE clear_io(PORTD, 5)
#define tgl_LED_STATE toggle_io(PORTD, 5)
#define read_LED_STATE read_io(PORTD, 5)


/************************************************************************/
/* Registers' structure                                                 */
/************************************************************************/
typedef struct
{
	uint8_t REG_CONFIG;
	uint8_t REG_DEVICES_CONNECTED;
	uint8_t REG_REPEATER_STATUS;
	uint8_t REG_BATTERY_RATE;
	float REG_BATTERY;
	float REG_BATTERY_TH_LOW;
	float REG_BATTERY_TH_HIGH;
	uint16_t REG_BATTERY_CALIBRATION0;
	uint16_t REG_BATTERY_CALIBRATION1;
} AppRegs;

/************************************************************************/
/* Registers' address                                                   */
/************************************************************************/
/* Registers */
#define ADD_REG_CONFIG                      32 // U8     Device's configuration
#define ADD_REG_DEVICES_CONNECTED           33 // U8     Reads if the port has a device connected to (bitmask)
#define ADD_REG_REPEATER_STATUS             34 // U8     Check if device is a repeater or spreading internal timestamp
#define ADD_REG_BATTERY_RATE                35 // U8     Configure how oftne the battery calue is sent to computer
#define ADD_REG_BATTERY                     36 // FLOAT  Reads the current battery charge
#define ADD_REG_BATTERY_TH_LOW              37 // FLOAT  Sets the low threshold from where the battery should start to be charged
#define ADD_REG_BATTERY_TH_HIGH             38 // FLOAT  Sets the high threshold from where the battery stops to be charged
#define ADD_REG_BATTERY_CALIBRATION0        39 // U16    
#define ADD_REG_BATTERY_CALIBRATION1        40 // U16    

/************************************************************************/
/* PWM Generator registers' memory limits                               */
/*                                                                      */
/* DON'T change the APP_REGS_ADD_MIN value !!!                          */
/* DON'T change these names !!!                                         */
/************************************************************************/
/* Memory limits */
#define APP_REGS_ADD_MIN                    0x20
#define APP_REGS_ADD_MAX                    0x28
#define APP_NBYTES_OF_REG_BANK              20

/************************************************************************/
/* Registers' bits                                                      */
/************************************************************************/
#define B_START_BATTERY_CYCLE              (1<<0)       // Starts battery cycle to extend batteries life
#define B_START_DISCHARGE                  (1<<1)       // Starts to discharge right away
#define B_START_CHARGE                     (1<<2)       // Starts to charge right away
#define B_STOPS_ANY                        (1<<3)       // Stop any control of the battery and get back to normal function
#define B_REPEATER                         (1<<0)       // Device is a repeater
#define GM_BATTERY_RATE                    3            // Configures the rate at which the battery charge is sent
#define MSK_EACH_60SECONDS                 0            // Sent each minute
#define MSK_EACH_10SECONDS                 1            // Sent each 10 second
#define MSK_EACH_SECOND                    2            // Sent each second
#define MSK_NEVER                          3            // Not sent

#endif /* _APP_REGS_H_ */

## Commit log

2021-02-07 Added the PCB.
    [harp timestamp generator.brd, harp timestamp generator.sch]
2021-02-07 Added auxiliar files.
    [crystals.xlsx]
2021-02-08 Corrected buffers' enable.
    [harp timestamp generator Gen3.brd, harp timestamp generator Gen3.sch]
2021-02-11 Big updates. Very close to final design.
    [harp timestamp generator Gen3.brd, harp timestamp generator Gen3.sch]
2021-02-11 Added BOM.
    [harp timestamp generator Gen3 BOM.xlsx]
2021-02-11 Increased battery current draw to around 250 mA.
    [harp timestamp generator Gen3.brd, harp timestamp generator Gen3.sch]
2021-02-12 Updated files with the MPN.
    [harp timestamp generator Gen3.brd, harp timestamp generator Gen3.sch]
2021-02-26 Corrected X1 PN and PCB's orientation.
    [harp timestamp generator Gen3 BOM.xlsx, harp timestamp generator Gen3.brd, harp timestamp generator Gen3.sch]
2021-04-25 Added first firmware files.
    [registers.xls]
2021-04-25 Added an extra 100uF capacitor to +5_USB.
    [harp timestamp generator Gen3 BOM.xlsx, harp timestamp generator Gen3.brd, harp timestamp generator Gen3.sch]
2021-04-25 Added proper filtering to RESET line.
    [harp timestamp generator Gen3 BOM.xlsx, harp timestamp generator Gen3.brd, harp timestamp generator Gen3.sch]
2021-04-28 Corrected the discharge circuit.
    [harp timestamp generator Gen3 BOM.xlsx, harp timestamp generator Gen3.brd, harp timestamp generator Gen3.sch, registers.xls]
2021-05-03 Added replacements.
    [harp timestamp generator Gen3 BOM.xlsx]
2021-05-04 Decreased discharge current by ~60 mA to ~175 mA in average.
    [harp timestamp generator Gen3 BOM.xlsx, harp timestamp generator Gen3.brd, harp timestamp generator Gen3.sch]
2021-05-05 Added ability to initiate battery cycle using the external button.
    [registers.xls]
2022-03-30 Removed LOCK from configuration.
    [registers.xls]
2022-03-30 Removed POWER_GOOD and wake up from buttons' interrupts.
2022-05-04 Changed battery connection to a new location and added an ON/OFF button.
    [copper_bottom_l4.gbr, copper_inner_l2.gbr, copper_inner_l3.gbr, copper_top_l1.gbr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]
2022-05-04 Updated BOM and added front and rear panels.
    [copper_bottom.gbr, copper_top.gbr, gerber_job.gbrjob, harp timestamp generator Gen3 BOM.xlsx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]
2022-05-23 Updated front panel to reflect the right device version.
    [harp timestamp generator Gen3 front panel.brd, silkscreen_top.gbr]
